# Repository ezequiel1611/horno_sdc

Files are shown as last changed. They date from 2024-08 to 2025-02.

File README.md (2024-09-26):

# HornoESP32 1.0

En el marco de una beca de servicio del Laboratorio de Control de la UTN Facultad Regional Paraná se realizó una actualización de un horno usado con fines académicos de forma que ahora el mismo use una placa de desarrollo ESP32 DevKit V1 como microcontrolador dotando así al equipo de la capacidad de conexión a internet. El microcontrolador maneja la potencia del horno mediante el uso de un TRIAC con control de disparo por ángulo de fase y cuenta con un sensor DHT11 para monitorear la temperatura del horno. Mediante la implementación de una base de datos en tiempo real (RTDB por Real Time Database) a través de la plataforma de Google Firebase es que interactúan tanto el microcontrolador como la aplicación web desarrollada para el control y monitoreo del sistema. El microcontrolador realiza peticiones a la RTDB cada 5 segundos actualizando la información de la temperatura del horno y verificando si la potencia empleada es la seleccionada por el usuario, mientras que al mismo tiempo la aplicación web lee cada segundo de la RTDB la información de la temperatura y la muestra en un gráfico temporal además de proveerle al usuario de un control deslizable para seleccionar la potencia del horno en una escala del 0% al 100%.

# Control de Potencia

El control de disparo del TRIAC por ángulo de fase se basa en la conexión de la tensión de red con la carga en cualquier punto de la semionda de forma sincronizada, de forma que se puede "recortar" la tensión sinusoidal en sectores más pequeños regulando así la potencia aplicada a la carga.

En la siguiente imagen se puede ver que al entregar el 50% de la potencia a la carga el forma de onda sinusoidal se ve "recortada" a la mitad de cada semiciclo.
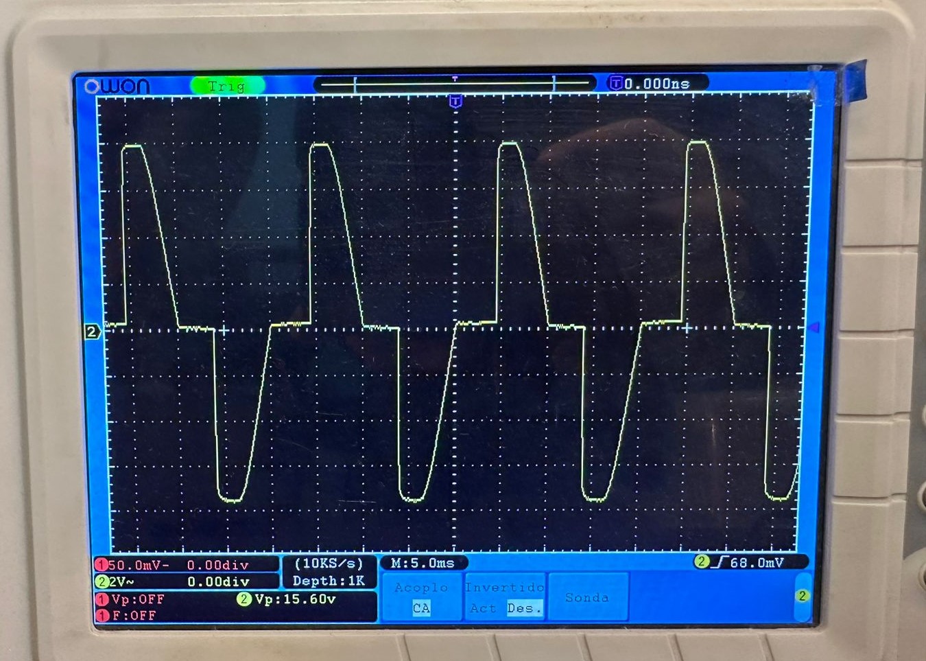
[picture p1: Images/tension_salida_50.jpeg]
Forma de Onda con 50% de la Potencia


El circuito empleado para lograr este funcionamiento es el siguiente:
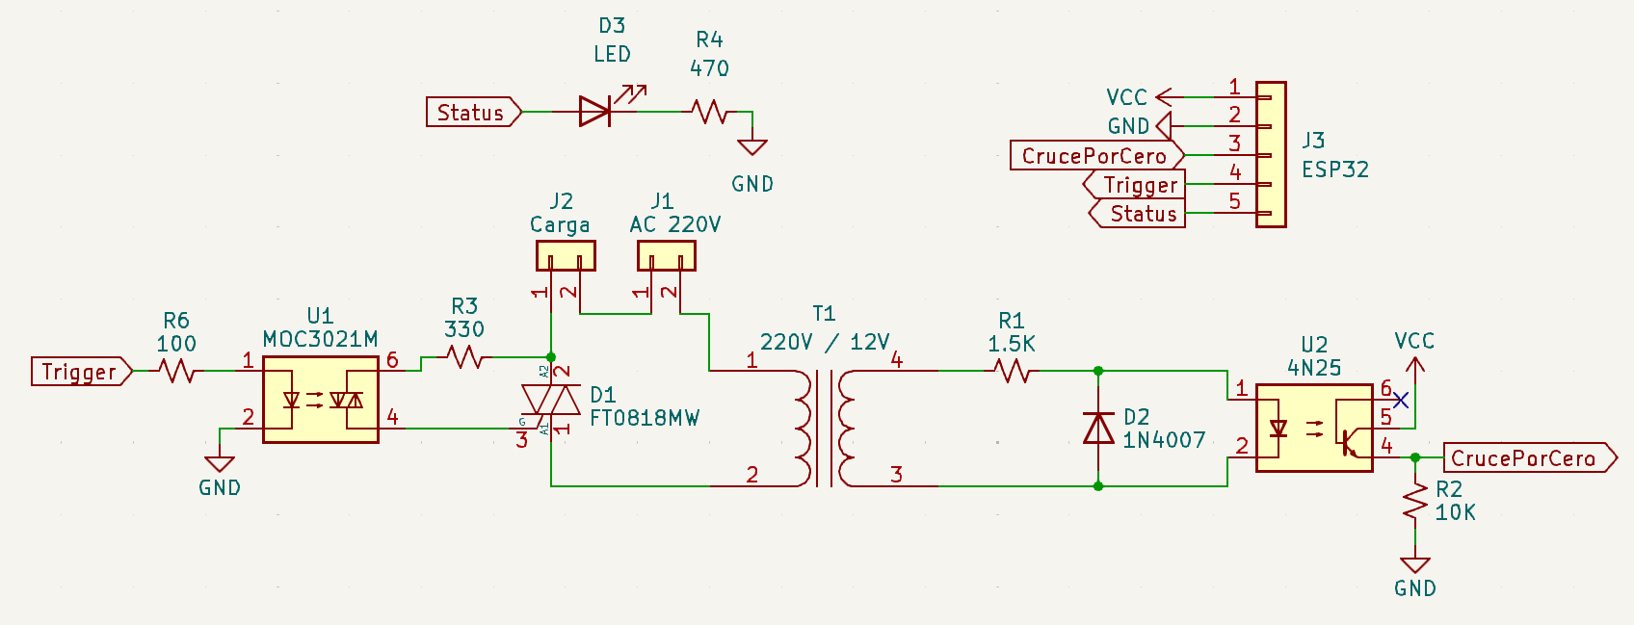
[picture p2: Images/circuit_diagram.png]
Circuito


Para más información sobre el diseño y teoría de funcionamiento del circuito, puede leer la documentación provista: [Teoría y Diseño Dimmer](https://github.com/ezequiel1611/horno_sdc/blob/main/Dimmer/TP2_Potencia.pdf)

# Introducción a Firebase y sus Beneficios

Firebase es una plataforma desarrollada por Google que ofrece una amplia gama de servicios para el desarrollo de aplicaciones móviles y web. Uno de los servicios más destacados que ofrece Firebase es su **base de datos en tiempo real**, que proporciona una solución eficiente para almacenar y sincronizar datos en tiempo real entre usuarios y dispositivos.

## Beneficios de usar la base de datos en tiempo real de Firebase:

1. **Sincronización en tiempo real:**  
   Los cambios realizados en la base de datos se reflejan instantáneamente en todos los dispositivos conectados. Esto facilita la creación de aplicaciones colaborativas y en tiempo real donde los usuarios pueden ver actualizaciones al instante.

2. **Facilidad de integración:**  
   Firebase ofrece bibliotecas para una variedad de plataformas y frameworks, lo que simplifica la integración en aplicaciones móviles y web existentes.

3. **Seguridad y autenticación:**  
   Firebase proporciona reglas de seguridad personalizables y autenticación integrada con otros servicios de Google, lo que ayuda a proteger los datos del usuario y controlar el acceso a la base de datos.

4. **Escalabilidad y disponibilidad:**  
   Al ser una plataforma en la nube administrada por Google, Firebase ofrece una alta escalabilidad y disponibilidad, sin preocuparse por la gestión de la infraestructura subyacente.

Firebase provee una facilidad a la hora de programar el microcontrolador ESP32 ya que con conectar el mismo a internet ya es posible interactuar con la base de datos de forma rápida e intuitiva debido a las librerías provistas para su uso. Por otro lado, también permite el alojamiento de una aplicación web permitiendo así el uso de un dominio en internet para crear una página web que sirva para control y monitoreo del sistema.

# Aplicación Web

Usando la herramienta de desarrollo online Replit se diseño la página web para monitorear y controlar el HornoESP32. Este desarrollo fue llevado a cabo en HTML y sus archivos HTML, CSS y JS puede accederse a través de: [Replit-HornoESP32](https://replit.com/@lautaroezequie3/HornoSDC)

## Monitoreo de la Temperatura

Al ingresar a la página usted verá un gráfico vacío, cuando haga click en el boton "On/Off" se habilitará la toma de datos y verá como cada segundo se imprime en la gráfica la temperatura del horno. Usted puede observar en tiempo real como varía la temperatura del horno mediante esta gráfica donde se indica en el eje X hora, minutos y segundos del dato tomado y en el eje Y la temperatura del horno en grados Celsius. Si quiere saber el valor exacto de un dato solo debe posar el mouse sobre el punto de la gráfica deseado, usted puede pausar la actualización de la gráfica haciendo click nuevamente en el botón "On/Off" si así lo desea.

Además de la visualización en tiempo real, la página web tiene un botón "Datos" el cual al presionarlo realiza la descarga de un archivo "datos.m" que contiene en cada renglón el dato de temperatura de cada punto de la gráfica. Esto con la finalidad de poder realizar un posterior análisis empleando GNU Octave o MatLab como se ve a continuación.

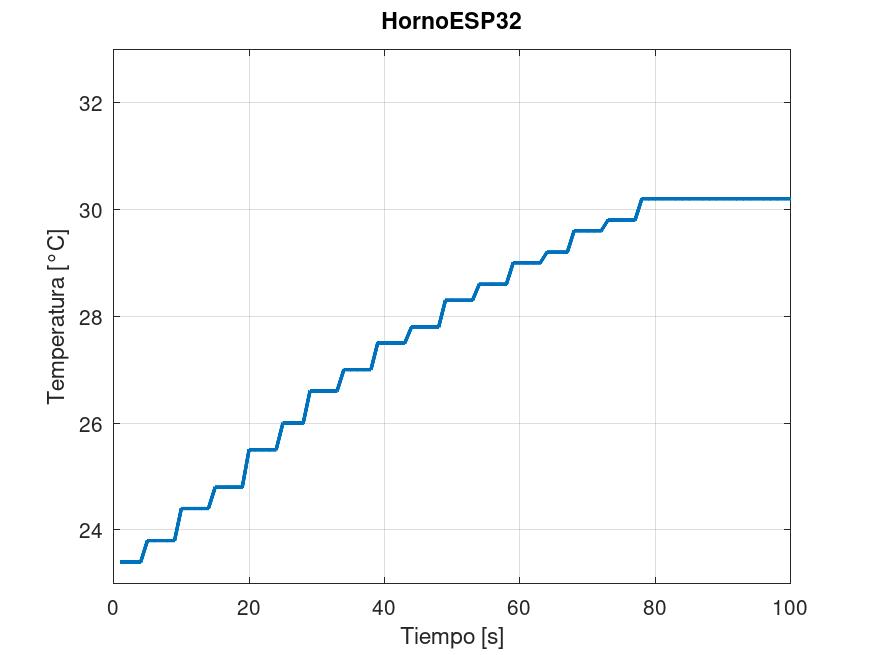
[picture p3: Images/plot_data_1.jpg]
test_octave


## Control de la Temperatura

Una vez en la página web usted podrá ver controlador deslizable que indica la potencia del horno en una escala del 0% al 100%, este controlador tiene un paso de 10% por lo que usted podrá determinar la potencia del horno a voluntad mediante la variación de este controlador deslizable. Este control deslizable envia el dato de a que ángulo se debe realizar el disparo del TRIAC a la base de datos y es el ESP32 el cual luego lee esta información y ajusta el ángulo de disparo al deseado para aśi establecer la potencia del horno a la requerida por el usuario.

**[Aplicación Web](https://horno-sdc.web.app/)**

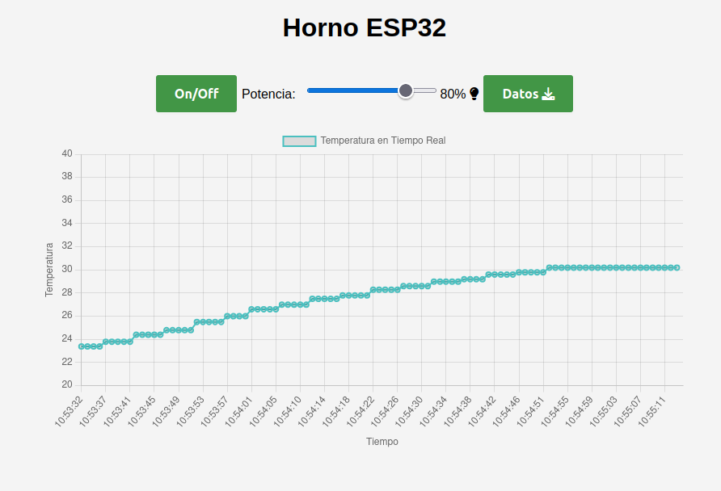
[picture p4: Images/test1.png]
preview app web


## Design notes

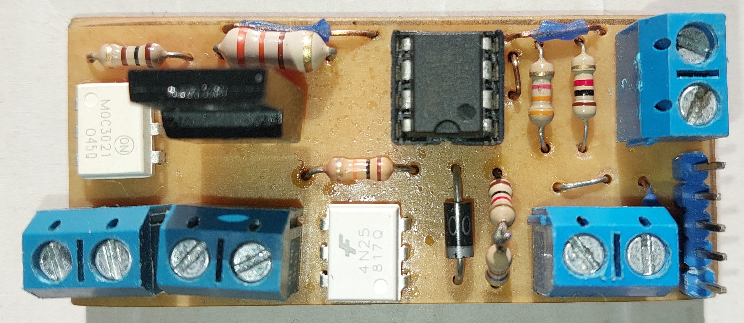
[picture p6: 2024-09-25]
Images/placa_anterior.jpg

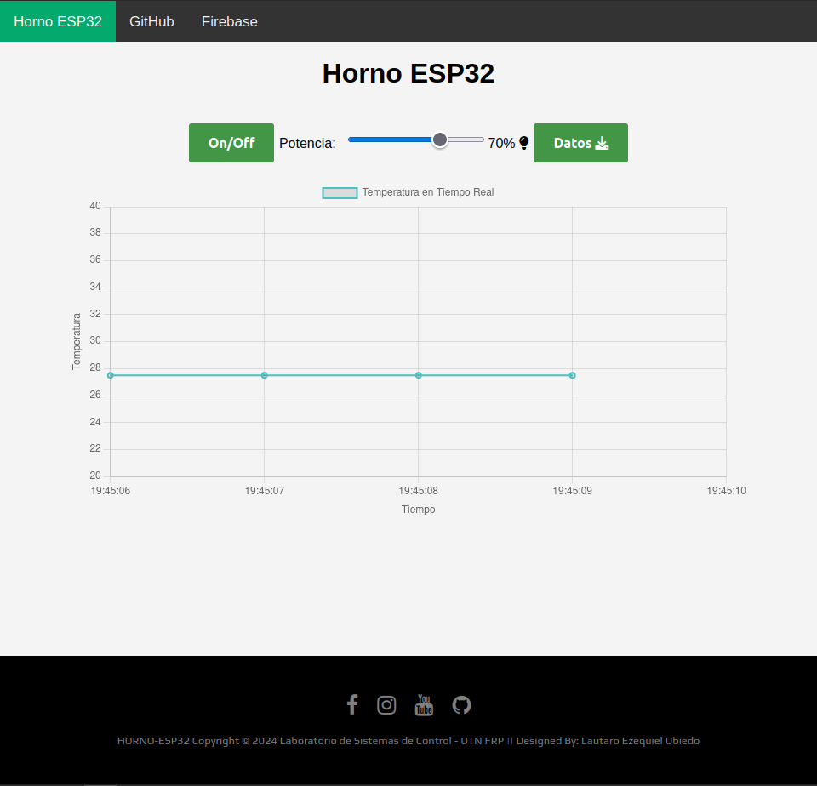
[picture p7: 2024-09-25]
Images/webapp_preview.png

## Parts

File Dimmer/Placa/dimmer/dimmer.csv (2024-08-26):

Source: | D:\5to Ingeniería Electrónica\Electrónica de Potencia\TP2\dimmer\dimmer.kicad_sch
Date: | 20/06/2023 15:16:13
Tool: | Eeschema 7.0.5
Component Count: | 16
Ref | Value | Footprint | Datasheet | Manufacturer | Vendor
Arduino1 | Conn_01x05 | Connector_PinSocket_2.54mm:PinSocket_1x05_P2.54mm_Vertical | ~
D1 | FT0818MW | Package_TO_SOT_THT:TO-220-3_Vertical | ~
D2 | 1N4007 | Diode_THT:D_DO-41_SOD81_P10.16mm_Horizontal | http://www.vishay.com/docs/88503/1n4001.pdf
J1 | AC | TerminalBlock:TerminalBlock_bornier-2_P5.08mm | ~
J2 | Carga | TerminalBlock:TerminalBlock_bornier-2_P5.08mm | ~
J3 | Trafo | TerminalBlock:TerminalBlock_bornier-2_P5.08mm | ~
J4 | Entrada_Control | TerminalBlock:TerminalBlock_bornier-2_P5.08mm | ~
R1 | 1.5K | Resistor_THT:R_Axial_DIN0207_L6.3mm_D2.5mm_P10.16mm_Horizontal | ~
R2 | 10K | Resistor_THT:R_Axial_DIN0207_L6.3mm_D2.5mm_P10.16mm_Horizontal | ~
R3 | 330 | Resistor_THT:R_Axial_DIN0207_L6.3mm_D2.5mm_P10.16mm_Horizontal | ~
R4 | 3.3K | Resistor_THT:R_Axial_DIN0207_L6.3mm_D2.5mm_P10.16mm_Horizontal | ~
R5 | 1K | Resistor_THT:R_Axial_DIN0207_L6.3mm_D2.5mm_P10.16mm_Horizontal | ~
R6 | 100 | Resistor_THT:R_Axial_DIN0207_L6.3mm_D2.5mm_P10.16mm_Horizontal | ~
U1 | MOC3021M | Package_DIP:DIP-6_W7.62mm_LongPads | https://www.onsemi.com/pub/Collateral/MOC3023M-D.PDF
U2 | 4N25 | Package_DIP:DIP-6_W7.62mm_LongPads | https://www.vishay.com/docs/83725/4n25.pdf
U3 | LM358 | Package_DIP:DIP-8_W7.62mm_LongPads | http://www.ti.com/lit/ds/symlink/lm2904-n.pdf

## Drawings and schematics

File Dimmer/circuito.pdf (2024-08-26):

U3:A

R3

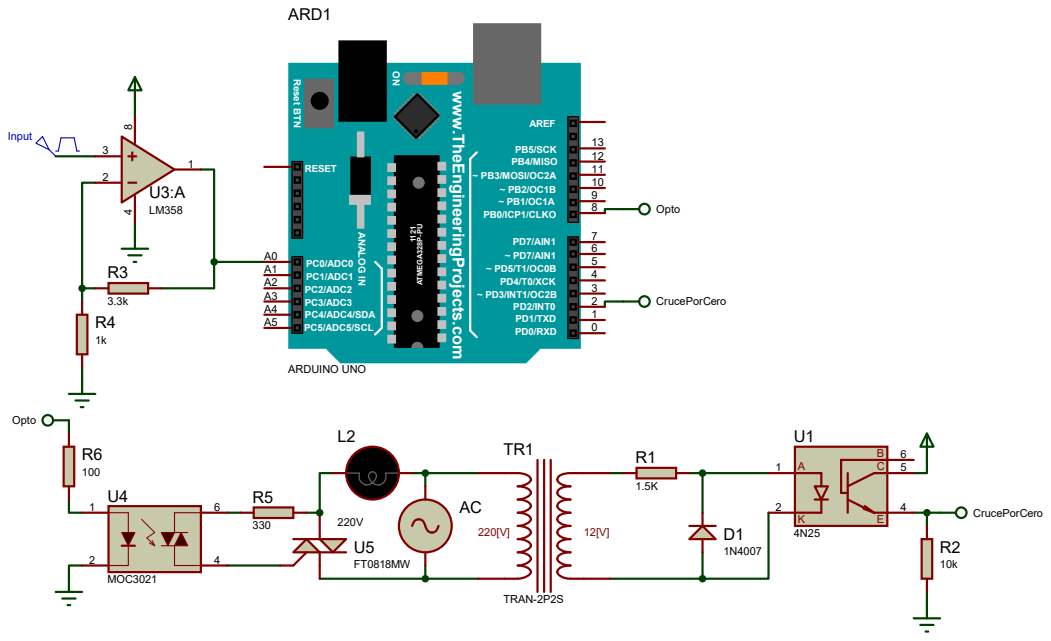
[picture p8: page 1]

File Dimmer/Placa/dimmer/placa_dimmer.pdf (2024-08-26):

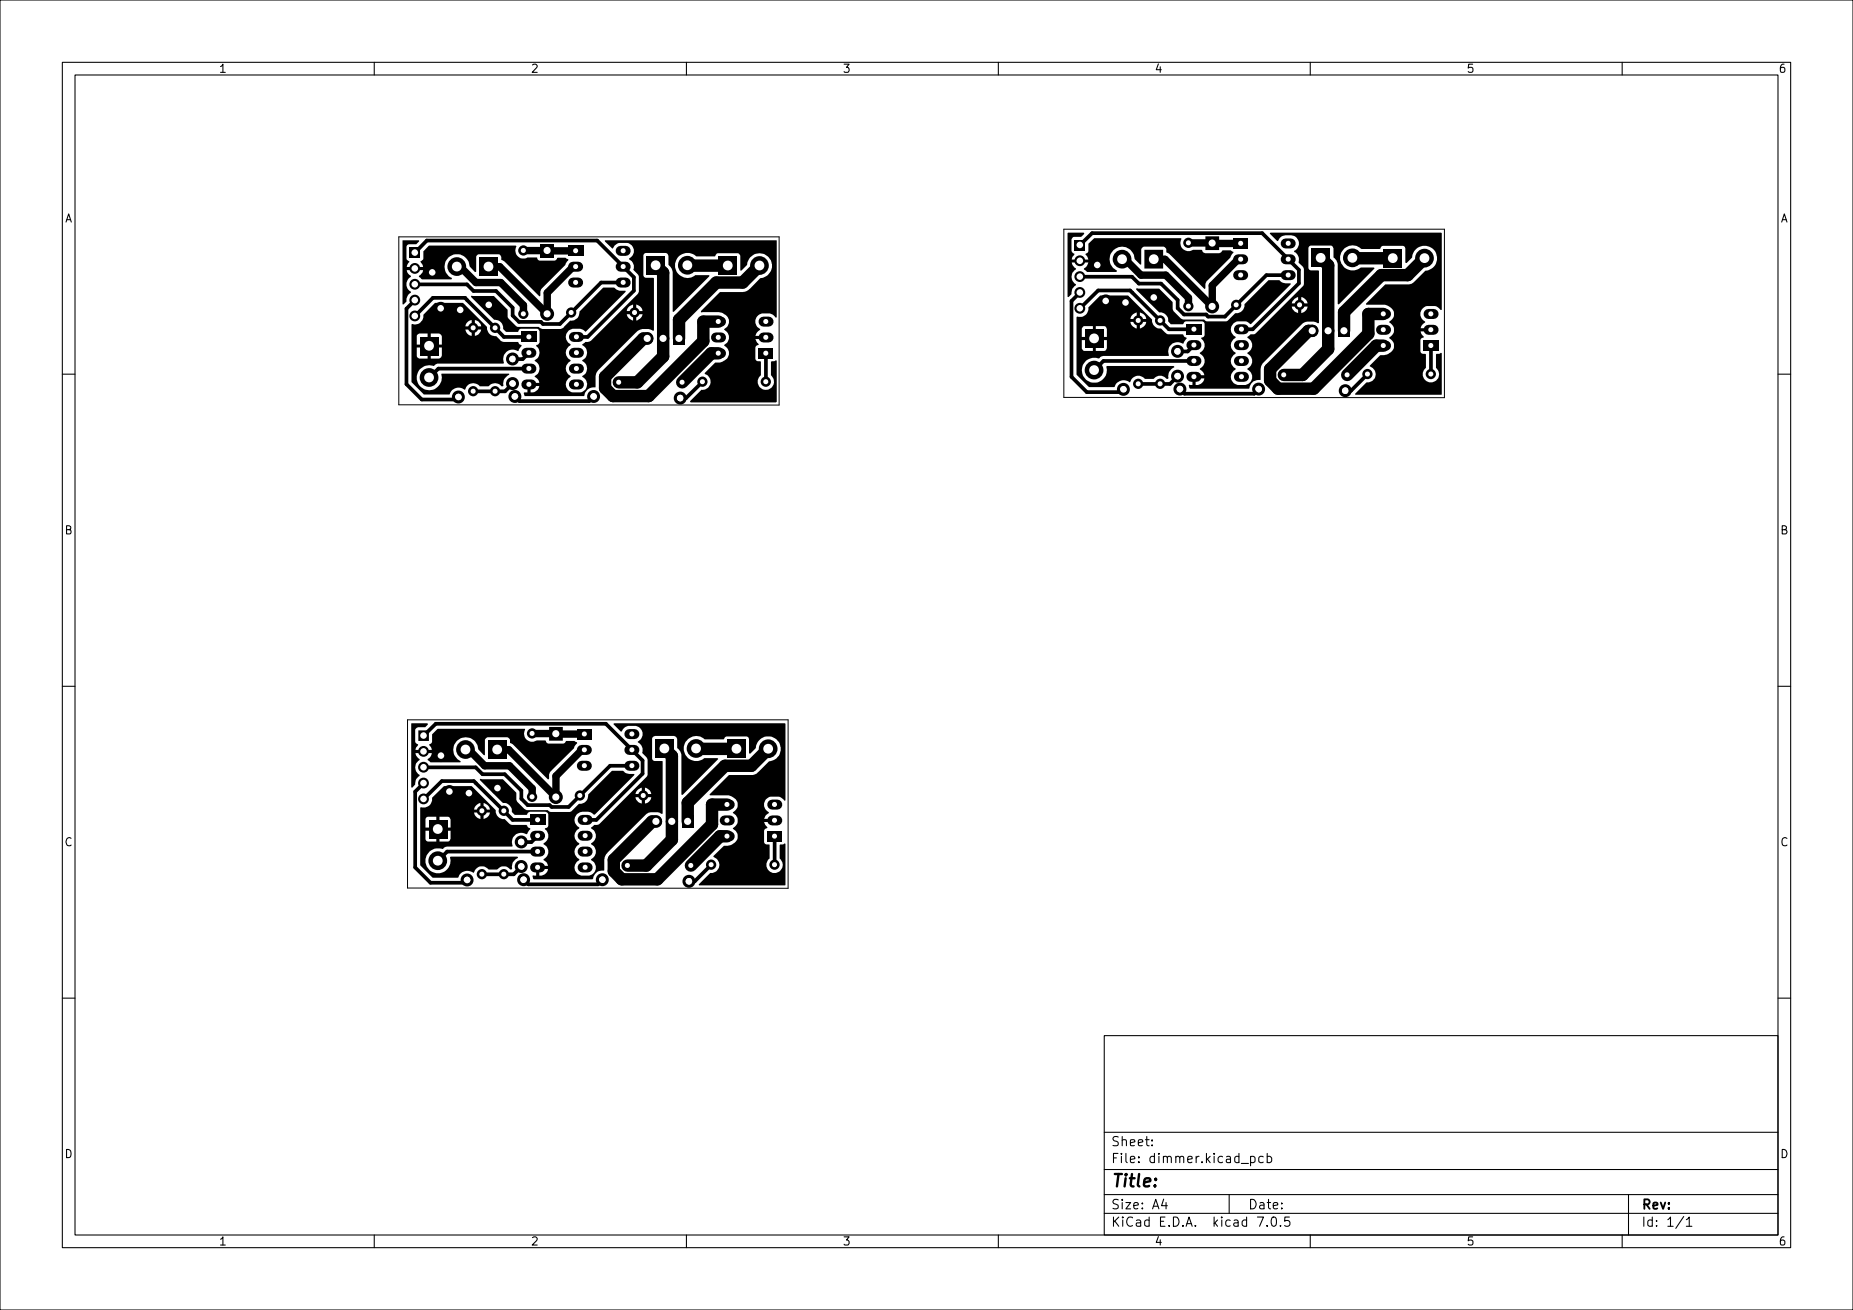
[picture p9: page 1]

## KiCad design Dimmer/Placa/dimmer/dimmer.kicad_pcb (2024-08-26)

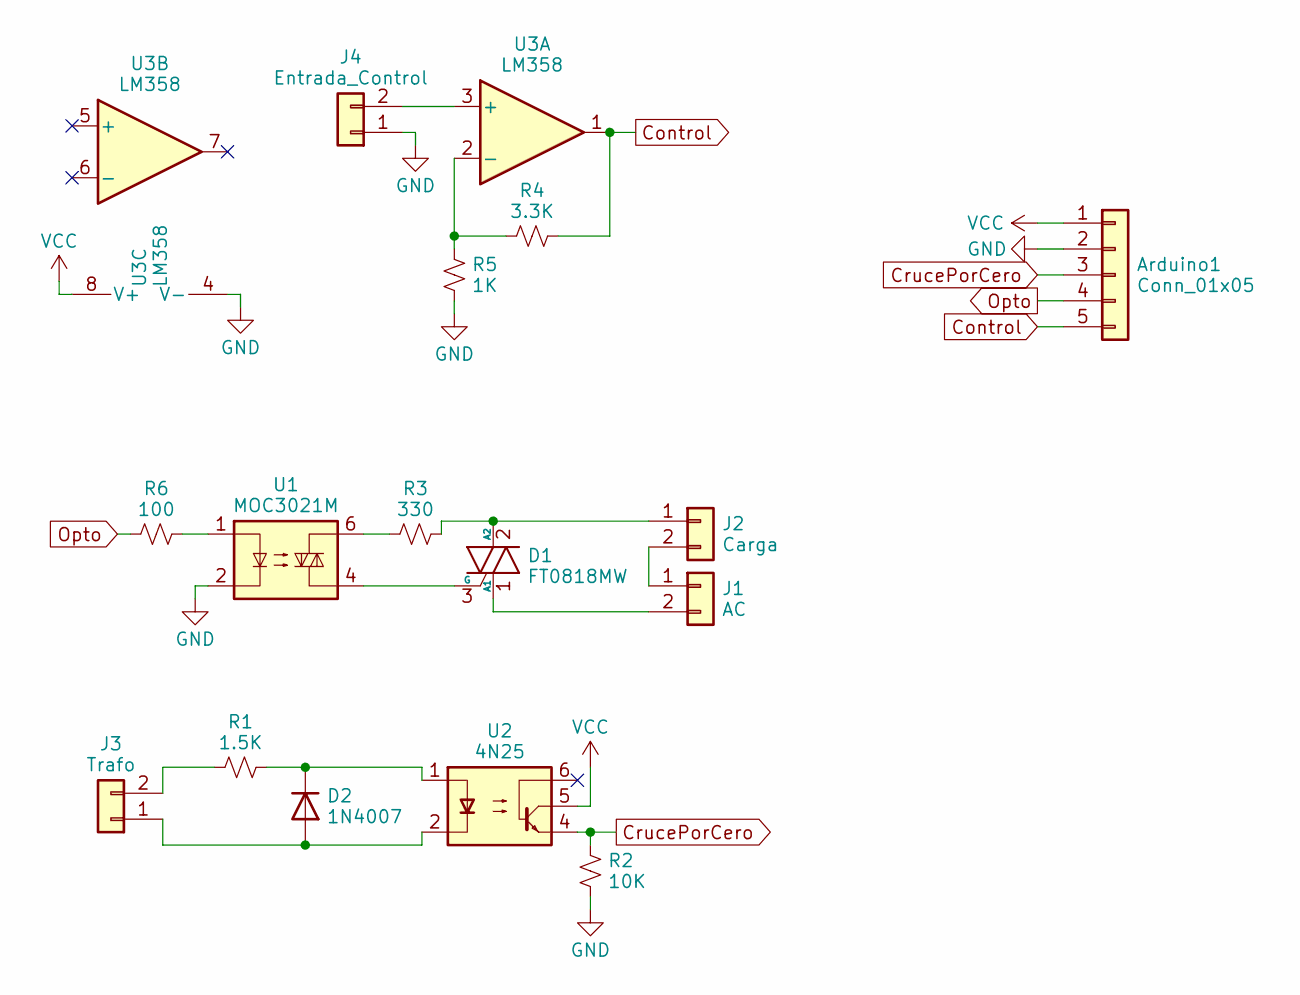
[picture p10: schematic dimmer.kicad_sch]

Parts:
Arduino1: Conn_01x05; PinSocket_1x05_P2.54mm_Vertical
D1: FT0818MW; TO-220-3_Vertical
D2: 1N4007; D_DO-41_SOD81_P10.16mm_Horizontal
J1: AC; TerminalBlock_bornier-2_P5.08mm
J2: Carga; TerminalBlock_bornier-2_P5.08mm
J3: Trafo; TerminalBlock_bornier-2_P5.08mm
J4: Entrada_Control; TerminalBlock_bornier-2_P5.08mm
R1: 1.5K; R_Axial_DIN0207_L6.3mm_D2.5mm_P10.16mm_Horizontal
R2: 10K; R_Axial_DIN0207_L6.3mm_D2.5mm_P10.16mm_Horizontal
R3: 330; R_Axial_DIN0207_L6.3mm_D2.5mm_P10.16mm_Horizontal
R4: 3.3K; R_Axial_DIN0207_L6.3mm_D2.5mm_P10.16mm_Horizontal
R5: 1K; R_Axial_DIN0207_L6.3mm_D2.5mm_P10.16mm_Horizontal
R6: 100; R_Axial_DIN0207_L6.3mm_D2.5mm_P10.16mm_Horizontal
U1: MOC3021M; DIP-6_W7.62mm_LongPads
U2: 4N25; DIP-6_W7.62mm_LongPads
U3: LM358; DIP-8_W7.62mm_LongPads

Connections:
Control: Arduino1.5, R4.2, U3.1
CrucePorCero: Arduino1.3, R2.1, U2.4
GND: Arduino1.2, J4.1, R2.2, R5.2, U1.2, U3.4 (V-)
unnamed: D1.1 (A1), J1.2
unnamed: D1.2 (A2), J2.1, R3.2
unnamed: D1.3 (G), U1.4
unnamed: D2.2 (A), J3.1, U2.2
unnamed: D2.1 (K), R1.2, U2.1
unnamed: J1.1, J2.2
unnamed: J3.2, R1.1
unnamed: J4.2, U3.3 (+)
unnamed: R3.1, U1.6
unnamed: R6.2, U1.1
unnamed: R4.1, R5.1, U3.2 (-)
Opto: Arduino1.4, R6.1
VCC: Arduino1.1, U2.5, U3.8 (V+)

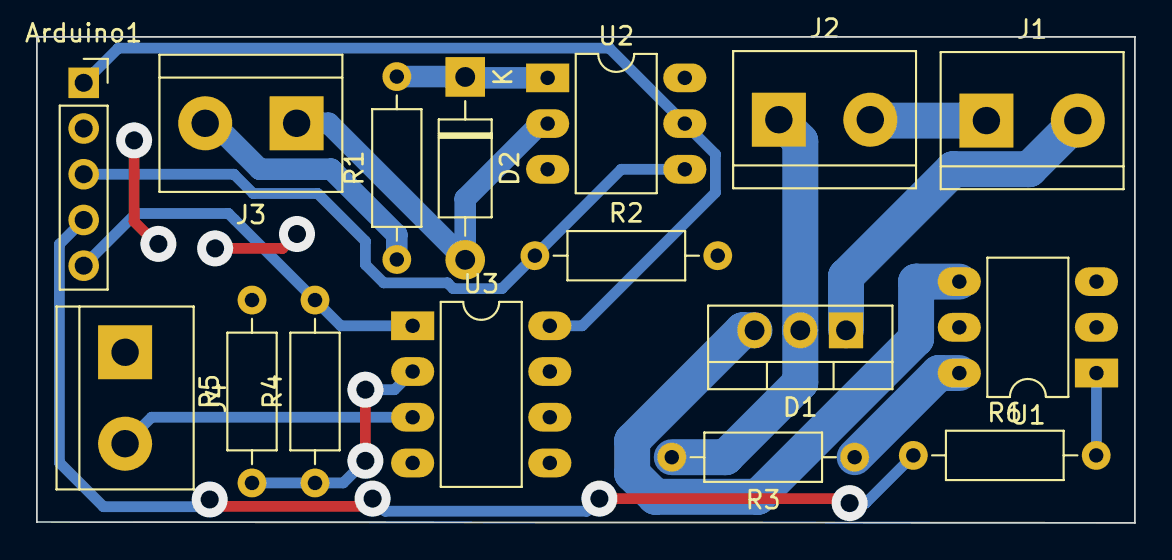
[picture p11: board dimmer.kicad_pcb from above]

Board: 2 copper layers, 61.0 x 27.0 mm, 16 parts (0 on the bottom side), 16 nets.

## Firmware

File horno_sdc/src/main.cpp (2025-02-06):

#include <Arduino.h>
#include <WiFi.h>
#include <Firebase_ESP_Client.h>
#include "addons/TokenHelper.h"
#include "addons/RTDBHelper.h"
/*
  Incluir estas dos librerias para usar el sensor DHT11 o DHT22
*/
//#include "DHT.h"
//#include <Adafruit_Sensor.h>
/*
  Incluir estas tres librerias para usar el BMP180 o BMP085
*/
#include <Wire.h>
#include <SPI.h>
//#include <Adafruit_BMP085.h>

// datos de red WiFi
#define WIFI_SSID "nombre_red"
#define WIFI_PASSWORD "clave_red"

// firebase API key
#define API_KEY "clave_api_firebase"

// url a la base de datos
#define DATABASE_URL "rtdb_url"

// datos de autenticación
#define USER_EMAIL "email_user"
#define USER_PASSWORD "clave_user"

// pines
#define TRIGGER 4  // Pin de disparo del optoacoplador
#define INTR_SYNC 18 // Pin de detección de cruce por cero
#define START 21    // Pin de encendido
//Adafruit_BMP085 bmp;  // GPIO22(D22)=SCL GPIO21(D21)=SDA
//#define DHTPIN 22   // Pin de lectura del sensor de temperatura
//#define DHTTYPE DHT11

// inicialización de la base de datos
FirebaseData fbdo;
FirebaseAuth auth;
FirebaseConfig config;

// inicialización del sensor DHT
//DHT dht(DHTPIN, DHTTYPE);

// variables
int potencia, disparo, ge = 0;
float t=30;
volatile bool onePulse = false;     // Bandera para segurar un disparo por semiciclo
unsigned long sendDataPrevMillis = 0;
bool startFlag = false; 

// timer
hw_timer_t *Timer0_Cfg = NULL;
hw_timer_t *Timer1_Cfg = NULL;

// declaracion de funciones
void IRAM_ATTR grado_electrico();
void IRAM_ATTR detector();

void setup() {
  // conexión a wifi
  WiFi.begin(WIFI_SSID, WIFI_PASSWORD);
  while(WiFi.status() != WL_CONNECTED){
    delay(300);
  }
  // configuración base de datos firebase
  config.api_key = API_KEY;
  config.database_url = DATABASE_URL;
  auth.user.email = USER_EMAIL;
  auth.user.password = USER_PASSWORD;
  Firebase.reconnectWiFi(true);
  fbdo.setResponseSize(4096);
  config.token_status_callback = tokenStatusCallback;
  config.max_token_generation_retry = 5;
  Firebase.begin(&config, &auth);
  // configuración de pines e interrupción externa
  pinMode(START, OUTPUT);
  pinMode(TRIGGER, OUTPUT);
  pinMode(INTR_SYNC, INPUT);
  attachInterrupt(INTR_SYNC, detector, CHANGE);
  // configuración del timer 0 para incrementar los grados eléctricos
  Timer0_Cfg = timerBegin(0, 45, true);
  timerAttachInterrupt(Timer0_Cfg, &grado_electrico, true);
  timerAlarmWrite(Timer0_Cfg, 99, true);
  digitalWrite(TRIGGER, LOW);
  // inicialización de la comunicación SPI con el BMP180
  //bmp.begin();
  // inicializacion del sensor DHT
  //dht.begin();
}

void loop() {
  // lectura del sensor de temperatura
  //t = bmp.readTemperature();
  //t = dht.readTemperature();
  // hago una petición a la base de datos
  if (Firebase.ready() && (millis() - sendDataPrevMillis > 5000 || sendDataPrevMillis == 0)){
    sendDataPrevMillis = millis();
    // envio de datoa a la base de datos
    Firebase.RTDB.setFloat(&fbdo, "READINGS/temperature", t);
    // toma de datos de la base de datos
    if(Firebase.RTDB.getInt(&fbdo, "/CONTROL/power/")){
      if(fbdo.dataType() == "int"){
        disparo = fbdo.intData();
      }
    }
    if(Firebase.RTDB.getBool(&fbdo, "/CONTROL/start/")){
      if(fbdo.dataType() == "boolean"){
        startFlag = fbdo.boolData();
        if(startFlag == true){digitalWrite(START, HIGH);}
        else{digitalWrite(START,LOW);}
      }
    }
  }
}

// put function definitions here:
void IRAM_ATTR detector() {
  ge = 0; // En cada cruce por cero se resetea la cuenta de los grados electricos
  onePulse = true;
  timerAlarmEnable(Timer0_Cfg);
}

void IRAM_ATTR grado_electrico(){
  ge++;
  if(disparo == ge && onePulse == true){
    onePulse = false;
    for(int i=0;i<20;i++) {
      digitalWrite(TRIGGER, HIGH); // Este for asegura que el pulso tenga la duración necesaria para activar el triac
    }
    digitalWrite(TRIGGER, LOW);
  }
}

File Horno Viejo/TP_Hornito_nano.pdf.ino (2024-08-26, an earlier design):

/*   Escalon al 60% 
     
     This example code is in the public domain.
*/

// These constants won't change.  They're used to give names
// to the pins used:
const int analogInPin = A0;  // Entrada analógica de la Temperatura
const int buttonPin = 2;     // the number of the pushbutton pin
const int ledPin =  13;      // the number of the LED pin
const int OutTriacPin =  4;  // D4 - Pin 20 para disparar el TRIAC
const int InCruceZero =  3;  // D3 - Pin 21 lee el detector de cruce por cero

int sensorValue = 0;         // value read from the LM335
int contador = 1;            // contador de lecturas
int buttonState = 0;         // variable for reading the pushbutton status
int parpadeo = 100;          // tiempo entre parpadeo del led
int Cruce0State = 0;         // Estado del cruce por cero

void setup() {
  // initialize serial communications at 115200 bps:
  Serial.begin(115200);
  // initialize the LED pin as an output:
  pinMode(ledPin, OUTPUT);
  // initialize the pushbutton pin as an input:
  pinMode(buttonPin, INPUT);
  // inicializa el disparo del TRIAC en bajo
  pinMode(OutTriacPin, OUTPUT);
  // inicializa la lectura del cruce por cero
  pinMode(InCruceZero, INPUT);
  // uso 3V3 con resistencias en serie para ajustar a 1V AREF
  analogReference(EXTERNAL);
  // activo la interrupción que dispara el cruce por cero.
  attachInterrupt(digitalPinToInterrupt (InCruceZero), cruzo, RISING);
}


// *************************************************
// se hace una especie de PWM sobre la base del
// período de tiempo de limiteOn + limiteOff
//
// limiteOn semiciclos encendido
// limiteOff semiciclos apagados
// limiteOn = limOn[k0];
// limiteOff = 5 - limOn[k0];
// cantRep es la cantidad de veces que repetimos PWM
// Tiempo del experimento es:
// cantRep*(limiteOn + limiteOff)/100 [segundos]

float cantRep[] = {1, 48000}; // TIEMPO QUE ESTARÁ ENCENSIDO en minutos
// 1200 es el factor de escala
int limOn[]   = {0, 1};  // INTENSIDAD DEL ENCENDIDO DEL FOCO DE 0 A 5
int CantElem  = 2;                          // CANTIDAD DE ESCALONES
int limiteOn;
int limiteOff;
int contOn = 0;
int contOff = 0;

bool encender = false;
void cruzo (void) {
  if (encender) {
    if (contOn < limiteOn) {
      digitalWrite(OutTriacPin, HIGH); // Prender Triac
      contOn ++;
      contOff = 0;
    }
    else {
      digitalWrite(OutTriacPin, LOW); // Apagar Triac
      if (contOff < limiteOff) {
        contOff ++;
      }
      else {
        contOn = 0;
      }
    }
  }
}

void loop() {
  int sumaCont = 0, sumaLim = 5, sumaPrev = 0;

  // parpadea el led esperado inicio con botón
  buttonState = digitalRead(buttonPin);
  while (buttonState == LOW) {
    digitalWrite(ledPin, LOW);
    delay (parpadeo / 4);
    buttonState = digitalRead(buttonPin);
    digitalWrite(ledPin, HIGH);
    delay (parpadeo / 4);
  }
  for (int k = 0; k < 5; k++) {
    digitalWrite(ledPin, LOW);
    delay (parpadeo);
    digitalWrite(ledPin, HIGH);
    delay (parpadeo);
  }
  digitalWrite(ledPin, LOW);
  buttonState = LOW;

  // *******************************************
  for (int k0 = 0; k0 < CantElem; k0++) {
    limiteOn = limOn[k0];
    limiteOff = 5 - limOn[k0];

    encender = true;
    for (int k = 0; k < cantRep[k0]; k++) {
      contOn = 0;
      contOff = 0;
      sumaCont = contOn + contOff;
  
      while ( sumaCont < sumaLim)
      {
        //  leo temperatura y transmito
        if (sumaCont != sumaPrev) {
          sensorValue = analogRead(analogInPin);
          Serial.print(limiteOn);
          Serial.print(" ");
          Serial.println(sensorValue);
          sumaPrev = sumaCont;
        }
        buttonState = digitalRead(buttonPin);
        if (buttonState != LOW) {
          Serial.print(0);
          Serial.print(" ");
          Serial.println(0);
          encender = false;
          digitalWrite(OutTriacPin, LOW); // Apagar Triac
          break;
       
      }
      sumaCont = contOn + contOff;
    }
  }
  encender = false;
  digitalWrite(OutTriacPin, LOW); // Apagar Triac
}
// *******************************************

while (1 < 2) {
  Serial.print(0);
  Serial.print(" ");
  Serial.println(0);
  delay(1);
}
}

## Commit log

2024-08-26 Archivos del módulo dimmer y código viejo del horno.
    Se añadieron los archivos de KiCad del módulo dimmer a usar, así como también el código empleado para su control, la teoría de diseño y funcionamiento y también los datasheets de los componentes empl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
    [dimmer.csv, dimmer.kicad_pcb, dimmer.kicad_sch]
2024-08-28 Primera versión del código
    Control de la potencia del foco usando un potenciómetro sin sensores de temperatura.
2024-09-25 HornoESP32 1.0
    Código para controlar el horno mediante ESP32 y comunicación con base de datos en tiempo real de Firebase.
2024-09-25 HornoESP32 1.0
    Ocultación de datos de api.
2024-09-25 App Web para el HornoESP32 1.0
    App Web para controlar y monitorear el HornoESP32 1.0
2024-09-25 Multimedia
    Imágenes añadidas para el README
2024-09-26 Test de analisis de datos
    Primera prueba de exportación de datos de la RTDB y su uso en el entorno de GNU Octave
2024-10-10 Adaptación para usar DHT11 o BMP180 a elección
2024-10-10 Integración de la librería Adafruit para BMP180
2025-02-06 Actualización de Seguridad
    Ahora el ESP32 debe autenticarse en el servidor para poder escribir en la base de datos.
2025-02-06 Cambios de Seguridad para la AppWeb
    Ahora la página web solicita un correo y contraseña para poder interactuar con el horno y visualizar los datos.
2025-02-06 Cambios de Seguridad
    Se eliminaron las claves de autenticación para mayor seguridad.
